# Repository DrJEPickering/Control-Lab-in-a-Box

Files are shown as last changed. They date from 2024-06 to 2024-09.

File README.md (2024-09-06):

Open in MATLAB Online (https://matlab.mathworks.com/open/github/v1?repo=DrJEPickering/Control-Lab-in-a-Box)

# Control-Lab-in-a-Box (CLB)
Dr James E. pickering, Aston University, Birmingham, United Kingdom
<br />E-mail: j.pickering1@aston.ac.uk

# Contents
<br />1.0 Aim of CLB
<br />2.0 Setting-Up
<br />3.0 Teaching Curriculum
<br />4.0 CLB Exercises 
<br />5.0 Trial CLB for Educators and Industry
<br />6.0 Publications Leading to the Development of CLB
<br />7.0 Other MATLAB and Simulink Projects of Interest
<br />8.0 Acknowledgements

## 1.0 Aim of CLB
CLB has been designed to: 
* Bridge the gap between control theory and practice
* Ensure that the skills and knowledge acquired from CLB are transferable, such as to a robotic platform
* Facilitate an incremental and practical approach to learning
* Teach students industry relevant processes and softwares 
* Be easily stored in a lab or office and portable enough to fit within a typical bag
* Affordable (approximately £100), thus reducing concerns if parts are broken or lost

  Presentation2 (https://youtu.be/RAiwTbeBUcU)

## 2.0 Setting-Up 
The computer-aided design (CAD) illustration below displays the setup of the Control-Lab-in-a-Box (CLB) with key components labeled. Please note that not all components are detailed in this diagram, e.g., nuts, bolts, and wires.

<br />For the CLB, rapid prototyping methods of 3D printing and laser cutting are employed, with the the 3D printing CAD files available [here](https://github.com/DrJEPickering/Control-Lab-in-a-Box/blob/main/CAD_files_for_3D_printing.zip) and the laser cutting CAD files available [here](https://github.com/DrJEPickering/Control-Lab-in-a-Box/blob/main/CAD_files_to_be_laser_cut.zip). For the CAD files, Solidworks 2023 files are provided, along with the correspondng STL files.

<br />A document detailing the parts/components necessary for the full utilisation of CLB is provided [here](https://github.com/DrJEPickering/Control-Lab-in-a-Box/blob/main/CLB_component_details.pdf). Additionally, a document detailing the assembly instructions and modifications for parts/components is included [here](https://github.com/DrJEPickering/Control-Lab-in-a-Box/blob/main/Assembly_modifications_Instructions.pdf)
 
ECC_2024_CLB_V4

## 3.0 Teaching Curriculum
The table below presents a schedule for integrating the Control-Lab-in-a-Box (CLB) exercises into the teaching of control engineering theory and simulation. Although the notes for theory and simulation are not provided on this page, they are available upon request via email.

Additionally, the MathWorks Onramp self-paced online courses for MATLAB and Simulink, used in the teaching curriculum, can be accessed through the provided [link](https://matlabacademy.mathworks.com/). 
The DC motor virtual lab is also available at the specified [link](https://uk.mathworks.com/matlabcentral/fileexchange/100064-virtual-hardware-and-labs-for-controls).

ECC_2024_CLB_V4

## 4.0 CLB Exercises 
Control-Lab-in-a-Box (CLB) is used for nine exercises (available to download via the links beneaf the illustration below), with these detailed via the illustration below. For the nine CLB exercises, Simulink Arduino Support Package is used, details can be found [here](https://uk.mathworks.com/hardware-support/arduino.html?#simulink). Details on how to install the Add-on (i.e., Simulink Arduino Support Package) can be found within CLB-1 (i.e., Simulink for Code Generation and Deployment: LED Exercise).

ECC_2024_CLB_V4

<br /> The nine CLB exercises can be viewed below:
<br />[CLB-1.1: Simulink for Code Generation and Deployment: LED Exercises](https://github.com/DrJEPickering/Control-Lab-in-a-Box/blob/main/CLB_1.1_Simulink%20for%20Code%20Generation%20and%20Deployment%20LED%20Exercise.pdf)
<br />[CLB-2.1: DC motor on/off, PWM and polarity control](https://github.com/DrJEPickering/Control-Lab-in-a-Box/blob/main/CLB_2.1_Polarity_speed_control_DC_motor.pdf)
<br />[CLB-3.1: Temperature sensor TMP36 and low pass filter](https://github.com/DrJEPickering/Control-Lab-in-a-Box/blob/main/CLB_3.1_Temp_sensor_filtered.pdf)
<br />[CLB-3.2: Ultrasonic sensor](https://github.com/DrJEPickering/Control-Lab-in-a-Box/blob/main/CLB_3.2_Ultrasonic_sensor.pdf)
<br />[CLB-3.3: DC motor with an encoder (Hall Effect Sensor)](https://github.com/DrJEPickering/Control-Lab-in-a-Box/blob/main/CLB_3.3%20dc_motor_encoder.pdf)
<br />CLB-4.1: TO be added SOON - DC motor proportional (P) speed control
<br />[CLB-4.2: Least squares for parameter estimation of a DC motor](https://github.com/DrJEPickering/Control-Lab-in-a-Box/blob/main/CLB_4.2%20system_indentification_for_parameter_estimation_dc_motor.pdf)
<br />[CLB-4.3: DC motor proportional and integral (PI) speed control](https://github.com/DrJEPickering/Control-Lab-in-a-Box/blob/main/CLB_4.3%20PI_control_of_a_DC_motor.pdf)
<br />[CLB-4.4: DC motor PI speed control with on/off safety aspects](https://github.com/DrJEPickering/Control-Lab-in-a-Box/blob/main/CLB_4.4%20Temp_disp_control_of_a_DC_motor.pdf)

For the above exercises, this [document](https://github.com/DrJEPickering/Control-Lab-in-a-Box/blob/main/compartment_part_details.pdf) will help when constructing the CLB rigs and perhaps also the CLB Components Details [document](https://github.com/DrJEPickering/Control-Lab-in-a-Box/blob/main/Assembly_modifications_Instructions.pdf).

## 5.0 Trial CLB for Educators and Industry
If you are interested in trying out CLB, we can post it to you. 
We kindly request that you return the box within a reasonable time period (e.g., 3 months) and provide user feedback. 
Please contact Dr. James E. Pickering via email at j.pickering1@aston.ac.uk.

If you do not have a MATLAB licence, a basic version of MATLAB Online is availble free. This provides 20 hours per month of free use and access to 10 commonly used products, see [link](https://uk.mathworks.com/products/matlab-online/matlab-online-versions.html).

## 6.0 Publications Leading to the Development of CLB
[Pickering, J.E. (2024). Developments in Control Engineering Education: Lab-in-a-Box Project Based Learning. In 2024 UKACC 14th International Conference on Control (CONTROL) (pp. 195-200). IEEE.](https://ieeexplore.ieee.org/document/10531946)

[Pickering, J.E. (2024). Control-Lab-in-a-Box: Bridging the Gap between Control Theory and Engineering Practice. UK and Ireland Engineering Education Research Network Conference Proceedings 2023.](https://journals.warwick.ac.uk/index.php/eern/article/view/1621)

## 7.0 Other MATLAB and Simulink Projects of Interest
[Arduino-based-bi-copter-experiments](https://github.com/eenikov/Arduino-based-bi-copter-experiments/tree/main)\
[Robotics 311: How to Build Robots and Make Them Move](https://github.com/michiganrobotics/rob311)

## Acknowledgments
Dr James E. Pickering wishes to acknowledge the following colleagues at Aston University for their help in developing Control-Lab-in-a-Box (CLB): Prof Keith J. Burnham, Aaisha Yasir (Design Intern), Stuart Hallard (Technician), David Palmer (Technician) and Amarjit Dhugga (Technician).

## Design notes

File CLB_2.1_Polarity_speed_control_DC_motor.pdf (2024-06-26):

# DC Motors On/Off, PWM and

# Contents

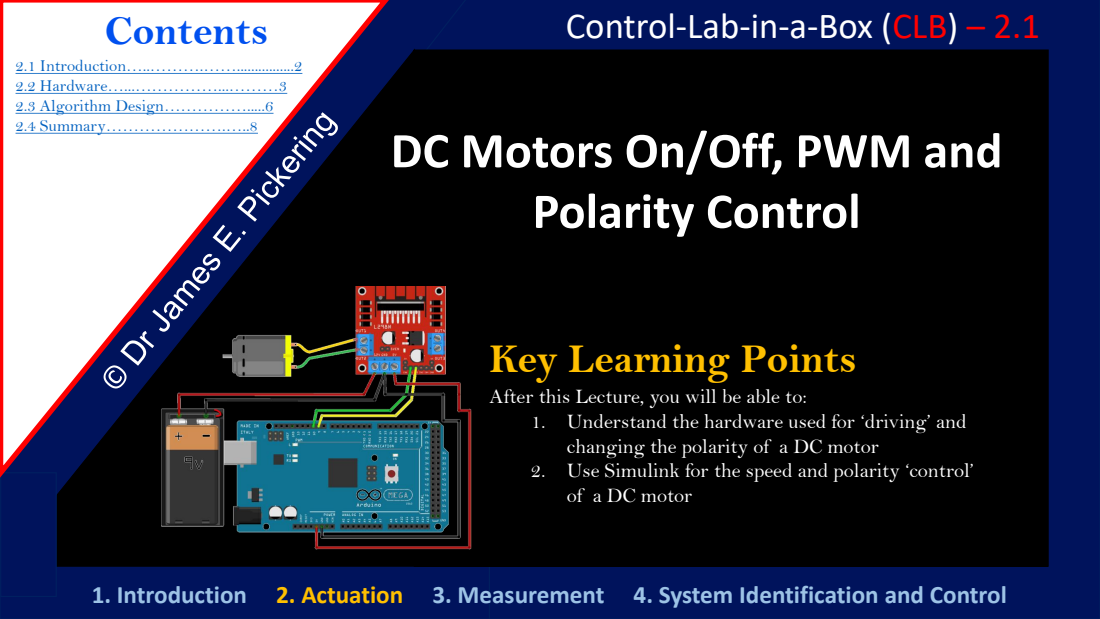
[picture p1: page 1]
Polarity Control; 2.1 Introduction…..……….……................2 2.2 Hardware…...……………...………3 2.3 Algorithm Design…………….....6 2.4 Summary………………….…..8; 1. Introduction 2. Actuation; 3. Measurement 4. System Identification and Control

Control-Lab-in-a-Box (CLB) – 2.1

Key Learning Points

After this Lecture, you will be able to:
1. Understand the hardware used for ‘driving’ and
changing the polarity of a DC motor
2. Use Simulink for the speed and polarity ‘control’
of a DC motor

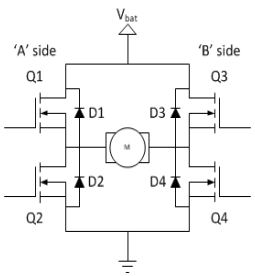
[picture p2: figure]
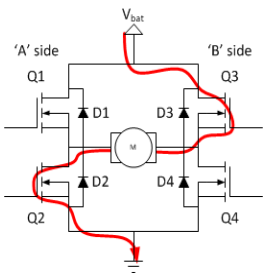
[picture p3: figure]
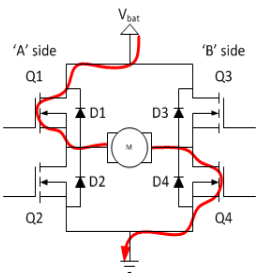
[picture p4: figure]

### 2.1 Introduction ▪ A H-bridge is an electronic

circuit that switches the
polarity of a voltage applied to a load, e.g., a DC motor

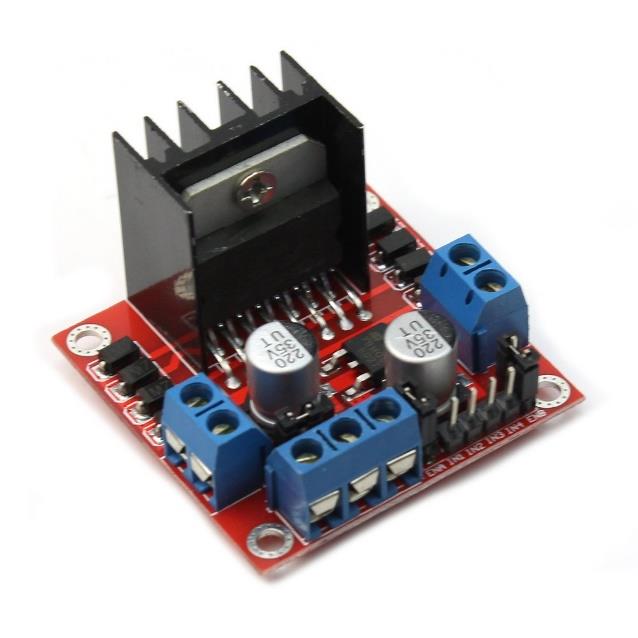
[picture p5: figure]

- The configuration of a H
bridge contains four switches, with the load at the centre, hence the H

-bridge
configuration
- All four switches can be turned on and off independently

© Dr James E. Pickering

DC Motor: PWM
& H

-Bridge

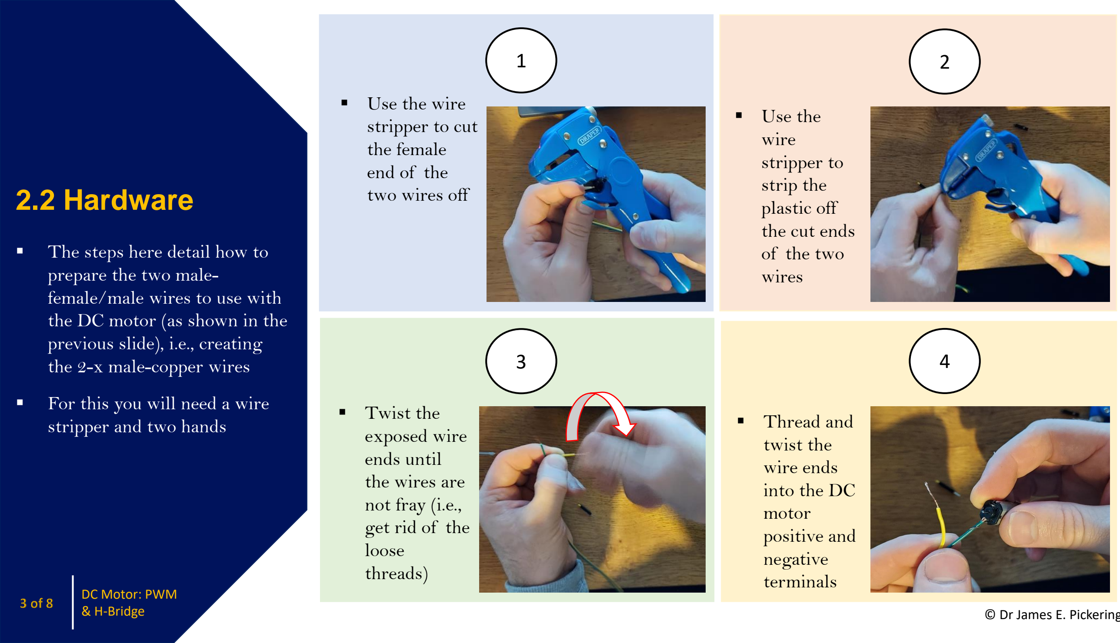
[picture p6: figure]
prepare the two male; - female/male wires to use with the DC motor (as shown in the previous slide), i.e., creating the 2; -x male; -copper wires; ▪ For this you will need a wire stripper and two hands; ▪ Use the wire stripper to strip the plastic off the cut ends of the two wires; ▪ Use the wire stripper to cut the female end of the two wires off; ▪ Twist the exposed wire ends until the wires are not fray (i.e., get rid of the loose threads); ▪ Thread and twist the wire ends into the DC motor positive and negative terminals; -Bridge

### 2.2 Hardware ▪ The steps here detail how to

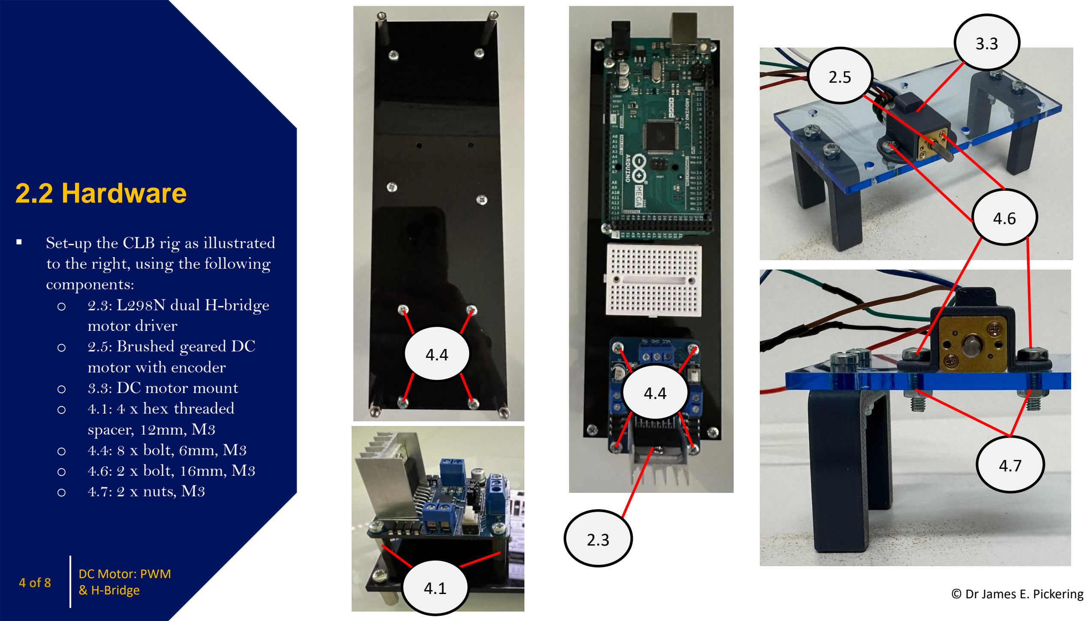
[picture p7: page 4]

### 2.2 Hardware ▪ Set-up the CLB rig as illustrated

to the right, using the following
components: o | | | 2.3: L298N dual H
-bridge
| | | motor driver
- 2.5: Brushed geared DC
| | | motor with encoder
- | 3.3: DC motor mount o | 4.1: 4 x hex threaded
| | | spacer, 12mm, M3
- | 4.4: 8 x bolt, 6mm, M3 o | 4.6: 2 x bolt, 16mm, M3 o | 4.7: 2 x nuts, M3
-Bridge | © Dr James E. Pickering

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
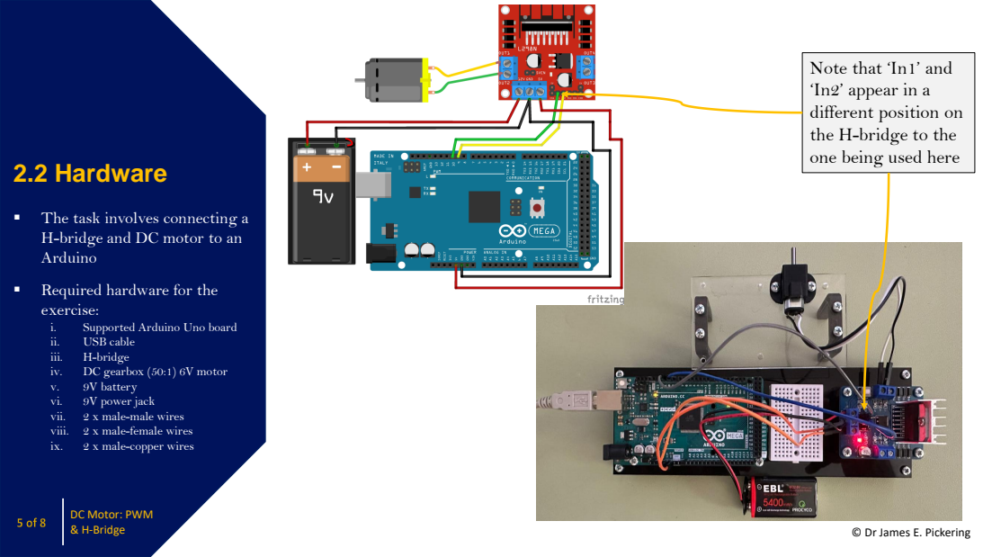
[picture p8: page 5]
2.2 Hardware ▪; The task involves connecting a H-bridge and DC motor to an; Arduino; USB cable; -bridge; DC gearbox; V motor; V battery; V power jack; x male; -male wires; -female wires; -copper wires; -Bridge

Note that ‘In1’ and
‘In2’ appear in a
different position on
the H
one being used here

-bridge to the

▪ Required hardware for the
exercise:
i. Supported Arduino Uno board
iii.
vii.
viii.

## 2.3 Algorithm Design

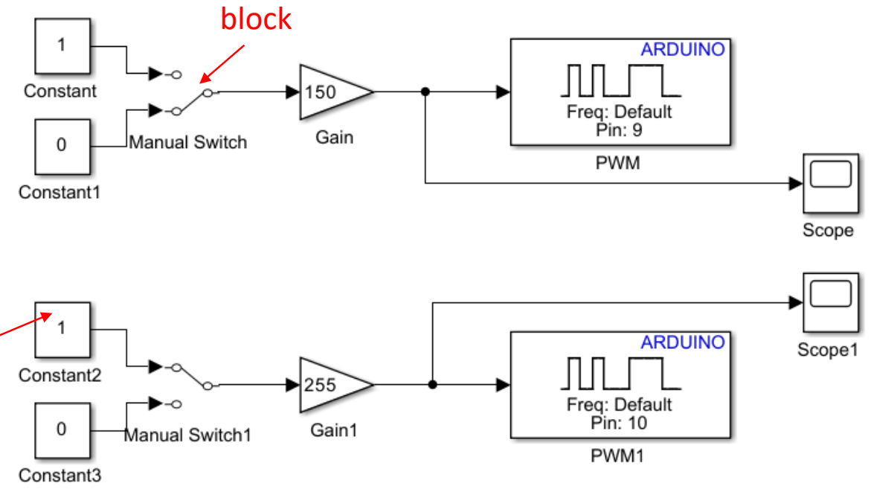
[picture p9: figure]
block

- The Simulink block diagram for the H-bridge algorithm design is given
- The logic for operating the ‘forward’ and ‘reverse’ motion of the DC motor is given
- Note that to realise this in real-time on a system, the switches would need to be external
- Logic of the H-bridge working: Forward
IN1 -> High
IN2 -> Low
Reverse
IN1 -> Low
IN2 -> High
Stop
Both are Low or High

& H-Bridge

### ‘Constant’ block

### ‘Manual Switch’

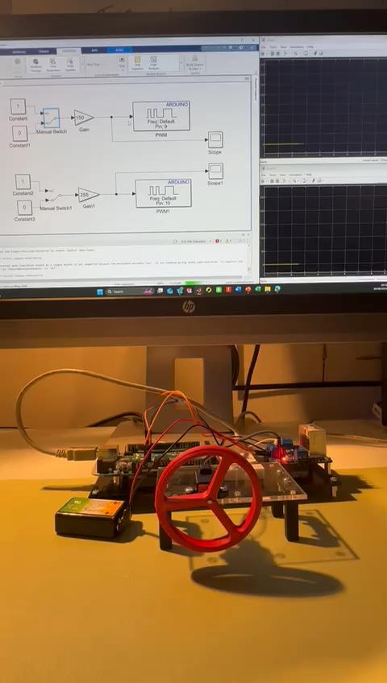
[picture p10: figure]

## 2.3 Algorithm Design

- Combines the pulse width modulation (PWM) and H-bridge

& H-Bridge

Control-Lab-in-a-Box (CLB): DC Motors On/Off, PWM
and Polarity Control

# Contents

# DC Motors On/Off, PWM and

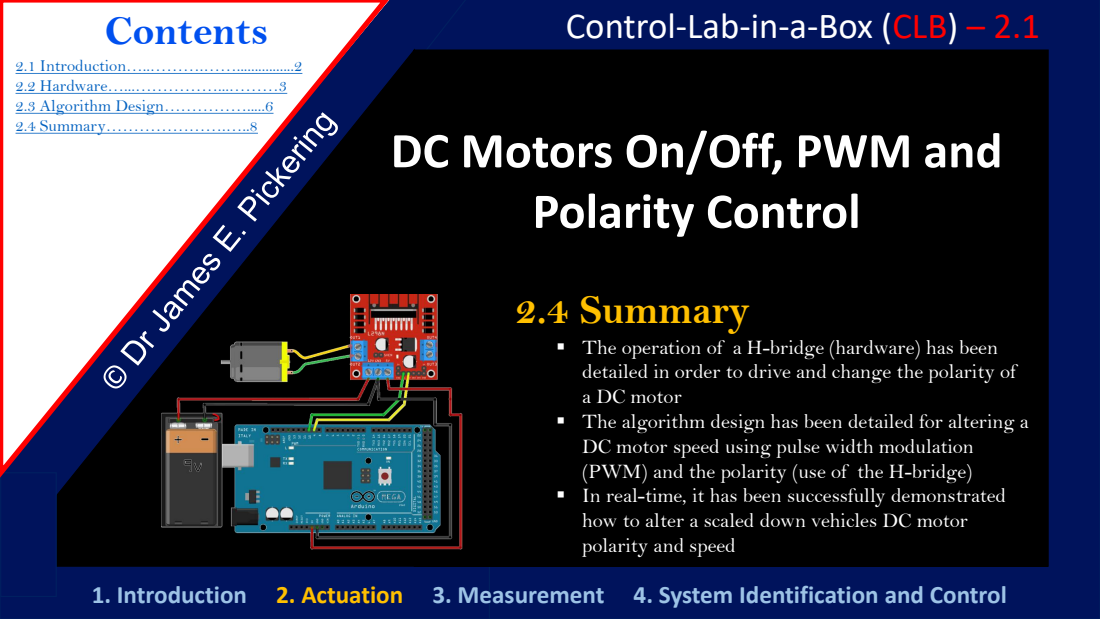
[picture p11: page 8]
2.4 Summary; 2.1 Introduction…..……….……................2 2.2 Hardware…...……………...………3 2.3 Algorithm Design…………….....6 2.4 Summary………………….…..8; 1. Introduction 2. Actuation; 3. Measurement 4. System Identification and Control; Polarity Control

Control-Lab-in-a-Box (CLB) – 2.1

▪ The operation of a H-bridge (hardware) has been
detailed in order to drive and change the polarity of
a DC motor
▪ The algorithm design has been detailed for altering a
DC motor speed using pulse width modulation
(PWM) and the polarity (use of the H-bridge)
▪ In real-time, it has been successfully demonstrated
how to alter a scaled down vehicles DC motor
polarity and speed

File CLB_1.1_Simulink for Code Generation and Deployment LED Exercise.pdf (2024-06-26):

# Simulink for Code Generation and

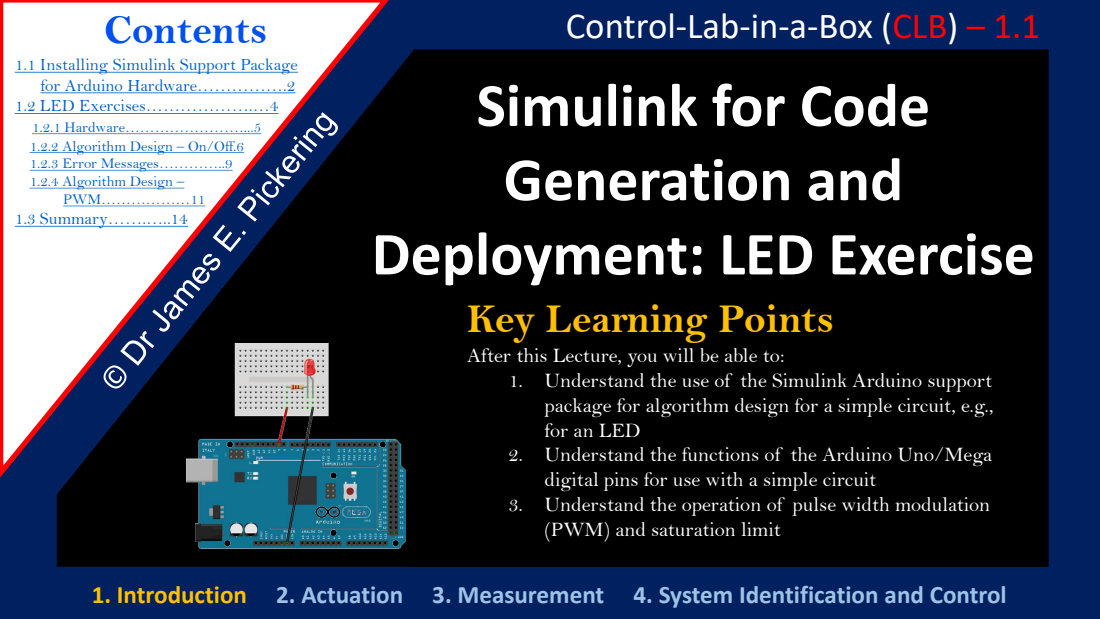
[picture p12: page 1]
1. Introduction 2. Actuation; 3. Measurement 4. System Identification and Control; Contents; 1.2.4 Algorithm Design –

Control-Lab-in-a-Box (CLB) – 1.1

1.1 Installing Simulink Support Package

1.2.2 Algorithm Design – On/Off.6

Deployment: LED Exercise

Key Learning Points

After this Lecture, you will be able to:
1. Understand the use of the Simulink Arduino support
package for algorithm design for a simple circuit, e.g.,
for an LED
2. Understand the functions of the Arduino Uno/Mega
digital pins for use with a simple circuit
3. Understand the operation of pulse width modulation
(PWM) and saturation limit

# 1.1 Installing Simulink Support Package for Arduino Hardware

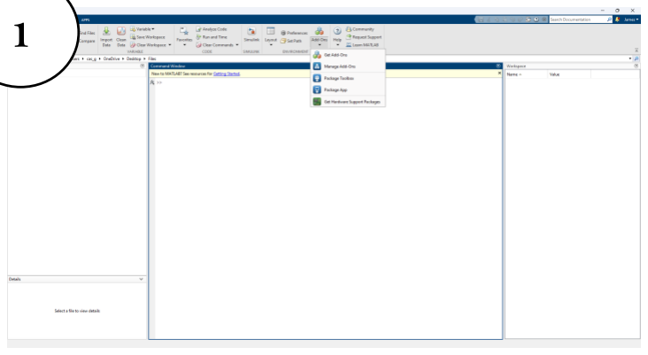
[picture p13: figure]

## - Undertake the following steps:

## 1) Click on ‘Add-Ons’ on the Toolbar and then ‘Get Hardware Support Package’

## 2) Search for the ‘Simulink Support Package for Arduino Hardware’ and click on it

## 3) Then click on ‘Install’ and then follow

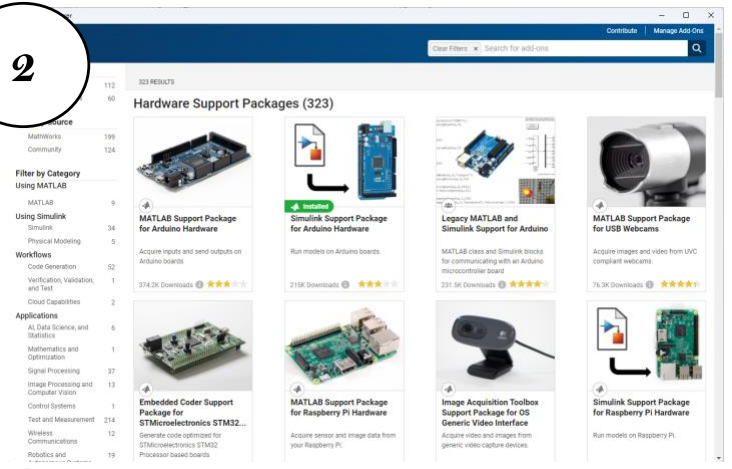
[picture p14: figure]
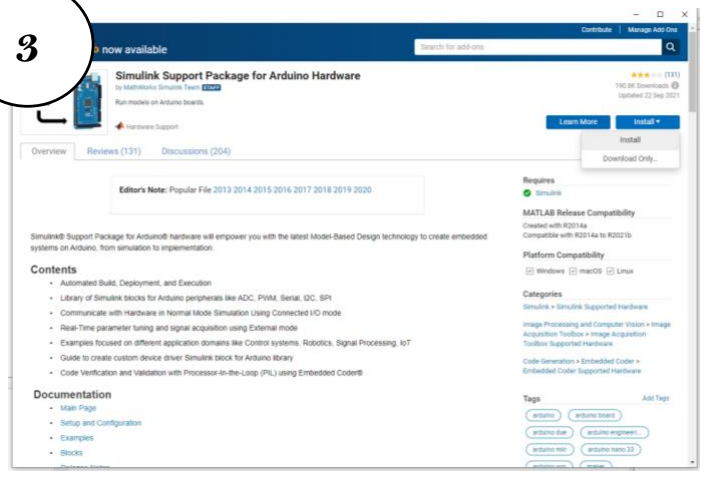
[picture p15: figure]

the steps-through | 3

© Dr James E. Pickering

Simulink for Autocode
Generation: LED
Exercise

## - Undertake the following steps: 4) After opening a ‘Blank Model’ within Simulink, open the ‘Library Browser’ – the

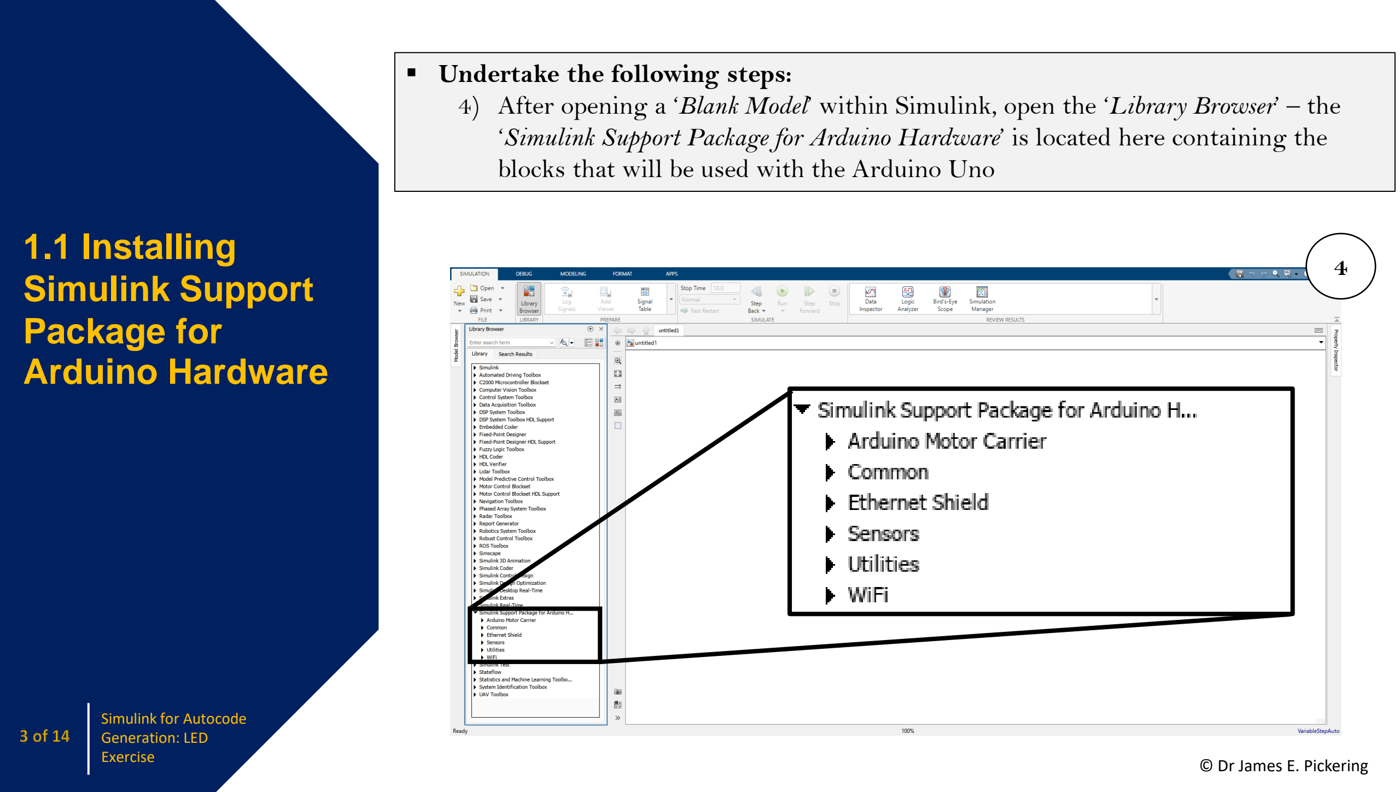
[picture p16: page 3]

## ‘Simulink Support Package for Arduino Hardware’ is located here containing the blocks that will be used with the Arduino Uno

# 1.1 Installing Simulink Support Package for Arduino Hardware

4

Simulink for Autocode

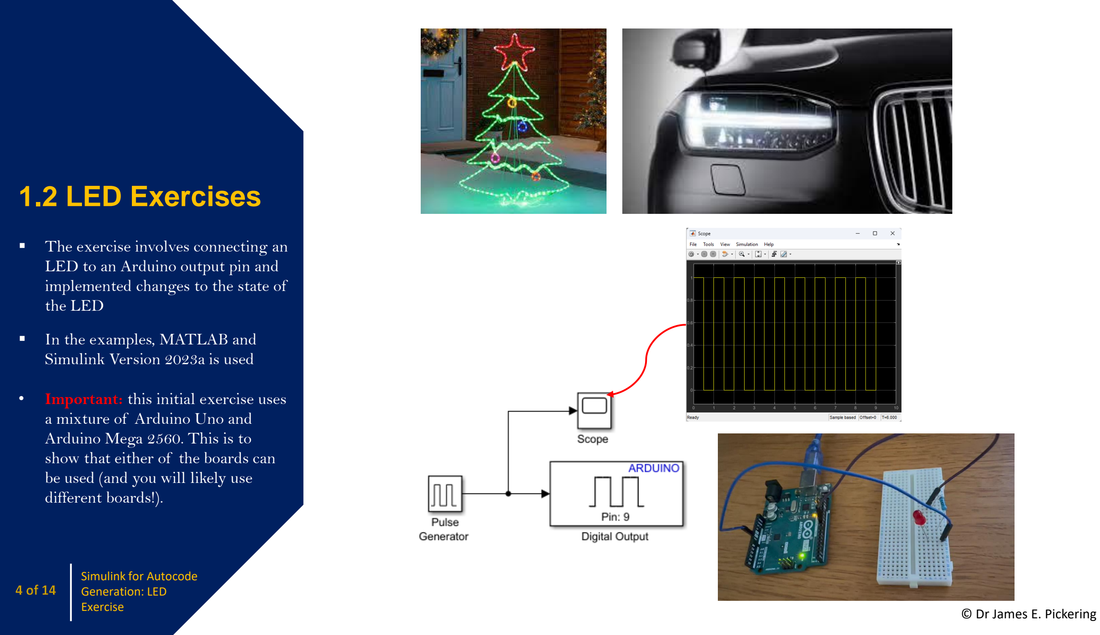
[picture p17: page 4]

### 1.2 LED Exercises ▪ The exercise involves connecting an

LED to an Arduino output pin and implemented changes to the state of the LED

- In the examples, MATLAB and Simulink Version 2023a is used
- Important: this initial exercise uses a mixture of Arduino Uno and Arduino Mega 2560. This is to show that either of the boards can be used (and you will likely use different boards!).

Simulink for Autocode

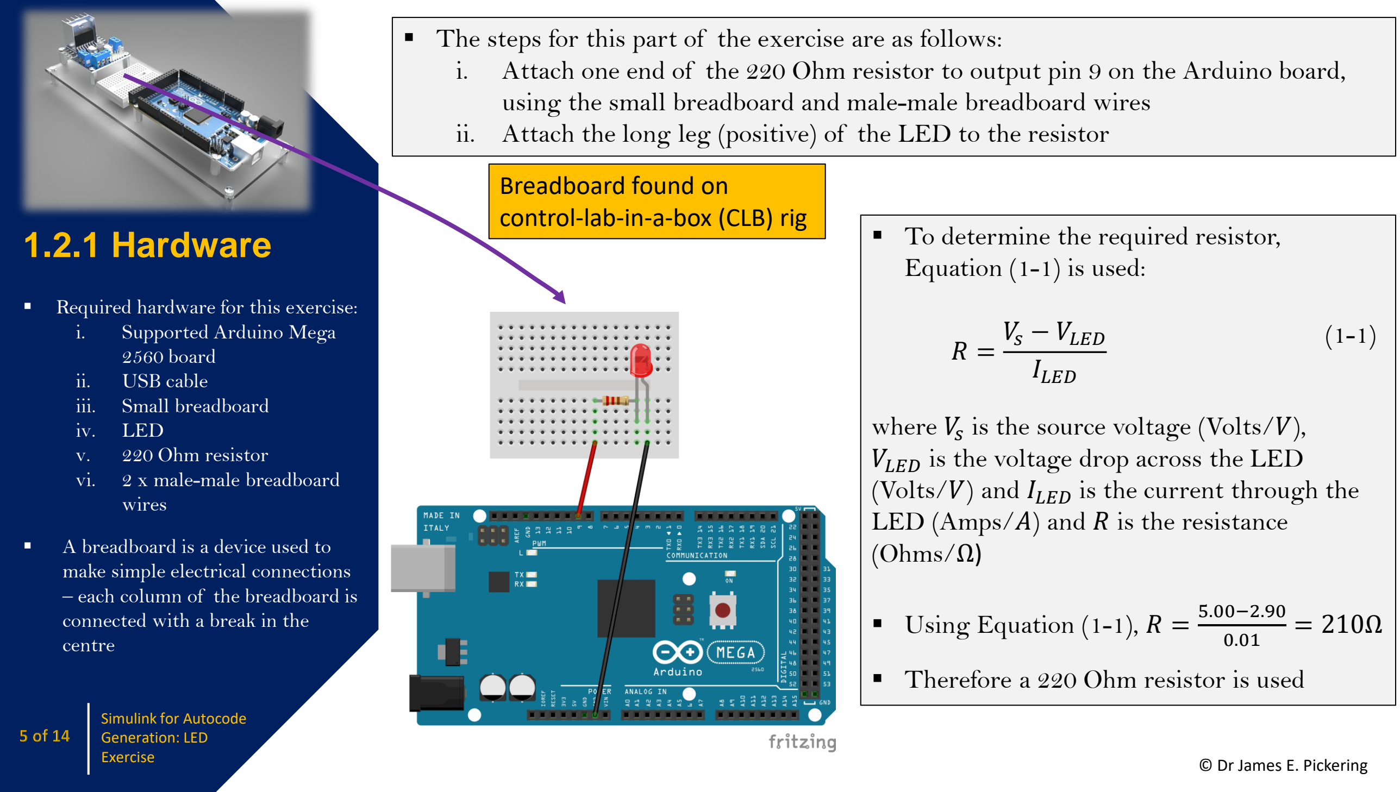
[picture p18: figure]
1.2.1 Hardware; ▪ Required hardware for this exercise: i. Supported Arduino Mega 2560 board; USB cable; iii.; Small breadboard; LED; v. 220 Ohm resistor; 2 x male-male breadboard; wires; ▪ A breadboard is a device used to make simple electrical connections – each column of the breadboard is connected with a break in the centre; ▪ To determine the required resistor, Equation (1-1) is used:; where Vs; is the source voltage (Volts/V), VLED is the voltage drop across the LED; LED (Amps/A) and R is the resistance (Ohms/Ω); ▪ Using Equation (1-1), R =; ▪ Therefore a 220 Ohm resistor is used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

## - The steps for this part of the exercise are as follows:

i. Attach one end of the 220 Ohm resistor to output pin 9 on the Arduino board,

## using the small breadboard and male-male breadboard wires ii. Attach the long leg (positive) of the LED to the resistor

## (Volts/V) and ILED is the current through the

# 1.2.2 Algorithm

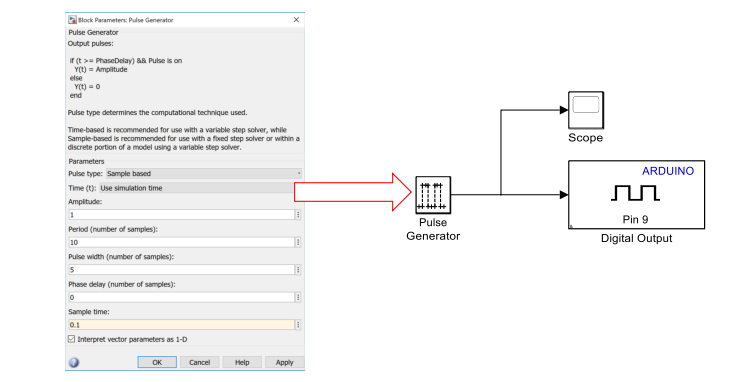
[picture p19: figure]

# Design – On/Off

- In this part of the exercise a Simulink model will be
developed to change the state of the Arduino digital output to being either on or off

- The steps for this part of the exercise are as follows: i. Set-up the pulse generator as shown below (found in ‘Sources’) and connect this to a digital output block (found under ‘Common’ in the ‘Simulink Support Package for Arduino Hardware’), with a scope connected (found in ‘Sinks’) ii. Amplitude of 1 implied a value of 5V will be supplied to Pin 9 (by default the ‘Digital Output’ block will be Pin 9)

Simulink for Autocode

# 1.2.2 Algorithm Design – On/Off

- In this part of the exercise, the Simulink model will be
configured and run on the
supported Arduino Uno/Mega board
- Important: make sure
MATLAB is operating/saving in a suitable working directory before clicking ‘Run’
1. Connect the Arduino board to your computer with a USB cable
2. When on your Simulink Window, click on ‘Modelling ‘ and then ‘Model Settings’ to open ‘Configuration Parameters’
3. Select the ‘Hardware Implementation’ panel and within the ‘Hardware Board’ tab, select the ‘Arduino Uno’ (or Arduino Mega 2560 – depending on the board being used) hardware from the ‘Hardware Board’ list, then click ‘Apply’ and then ‘OK’
4. Now in your Simulink model, the ‘Hardware’ tab will appear (Note: your Simulink model should be developed before undertaking this step). You should see the ‘Arduino Board’. Now change the simulation stop time to ‘inf ’ (infinity) and then click ‘Monitor & Tune’. The Simulink model (algorithm design) will now be deployed (converted to C code) to the connected Arduino hardware.
5. Look at the LED attached to pin 9. The LED should blink once time every second.
6. See the next slide if you’re experiencing errors

2 & 3

Linked board | Simulation stop time (i.e., infinity’)

4

## Embed code

Simulink for Autocode

## Arduino Mega 2560 can also be selected here

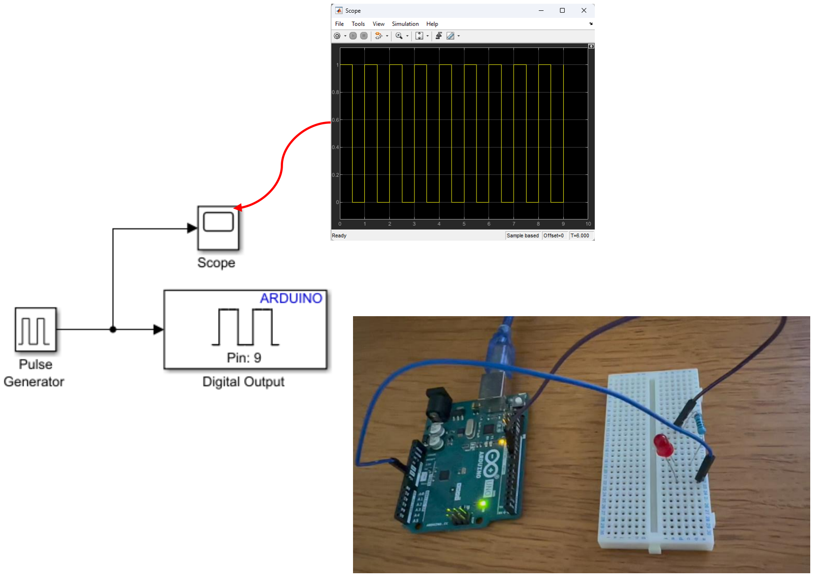
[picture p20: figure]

# 1.2.2 Algorithm Design – On/Off

Simulink for Autocode

1

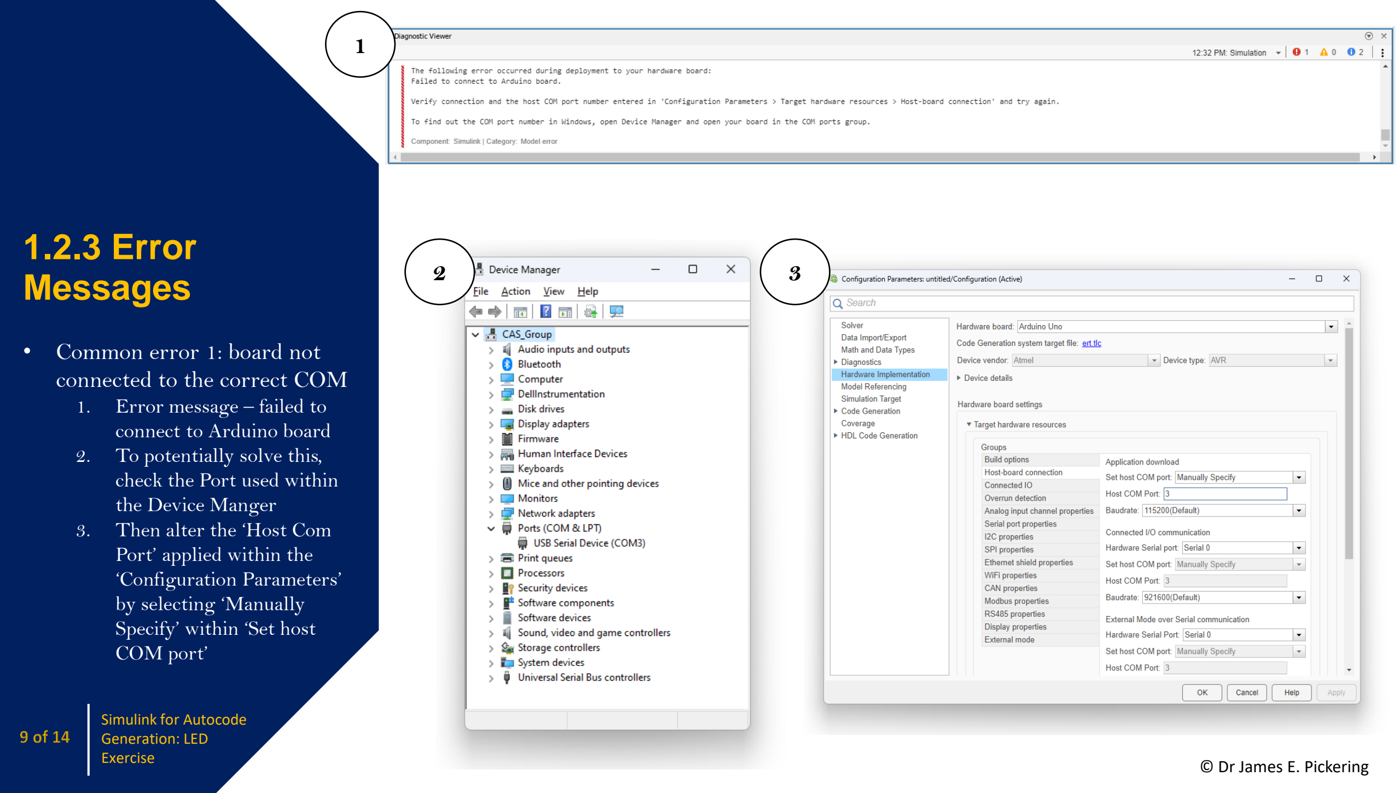
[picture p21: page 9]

# 1.2.3 Error

Messages • Common error 1: board not

connected to the correct COM
1. Error message

– failed to
connect to Arduino board
2. To potentially solve this, check the Port used within the Device Manger
3. Then alter the ‘Host Com Port’ applied within the
‘Configuration Parameters’ by selecting ‘Manually
Specify’ within ‘Set host
COM port’

2

3

Simulink for Autocode

1

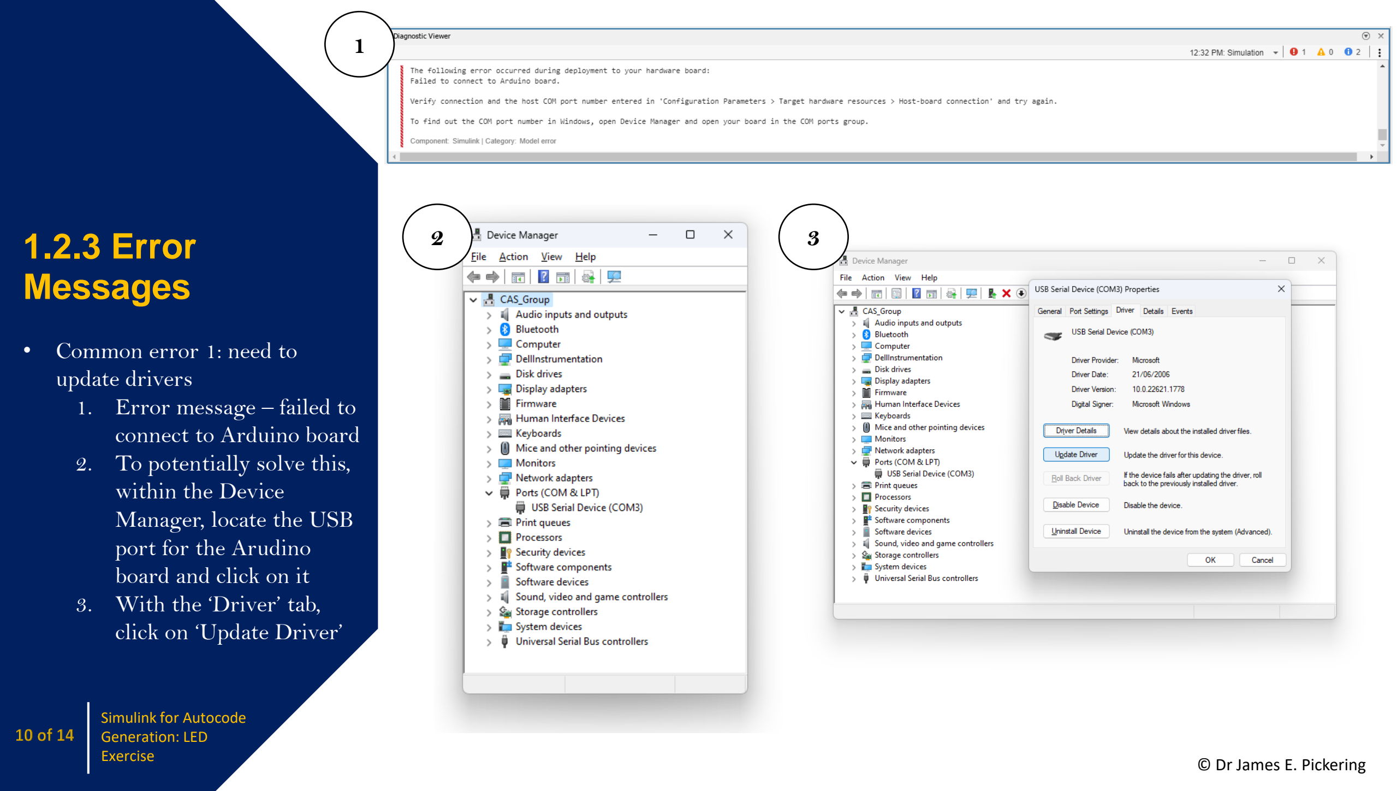
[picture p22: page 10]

# 1.2.3 Error

Messages • Common error 1: need to

update drivers
1. Error message

– failed to
connect to Arduino board
2. To potentially solve this, within the Device
Manager, locate the USB
port for the Arudino
board and click on it
3. With the ‘Driver’ tab,
click on ‘Update Driver’

2

3

Simulink for Autocode

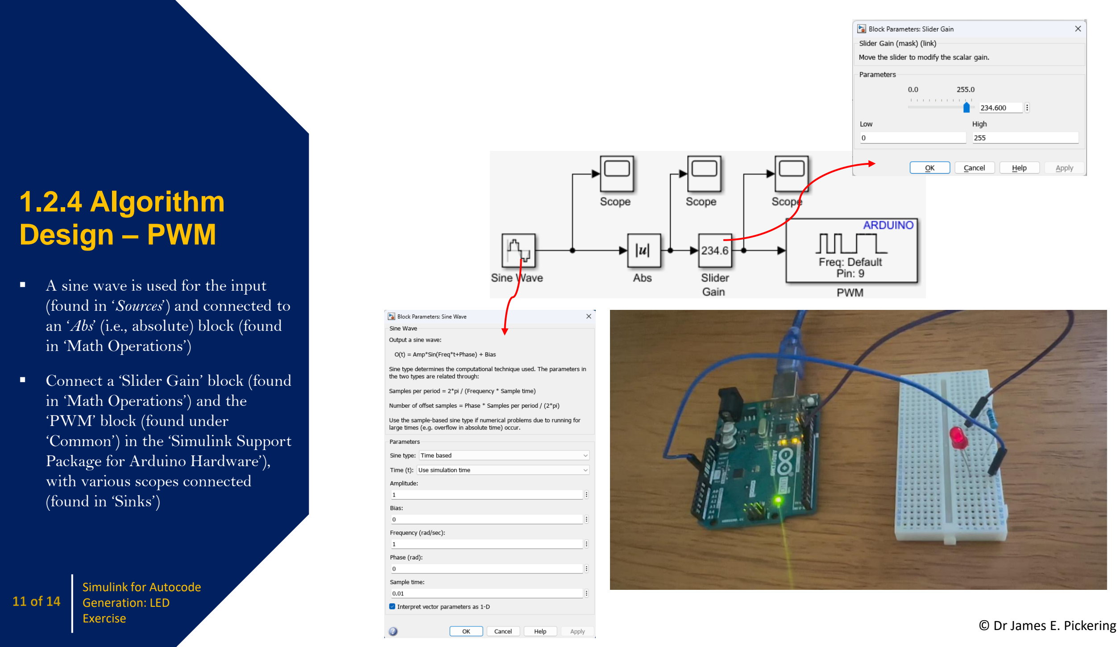
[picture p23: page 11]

# 1.2.4 Algorithm Design

# – PWM

- A sine wave is used for the input (found in ‘Sources’) and connected to an ‘Abs’ (i.e., absolute) block (found in ‘Math Operations’)
- Connect a ‘Slider Gain’ block (found in ‘Math Operations’) and the ‘PWM’ block (found under
‘Common’) in the ‘Simulink Support Package for Arduino Hardware’), with various scopes connected (found in ‘Sinks’)

Simulink for Autocode

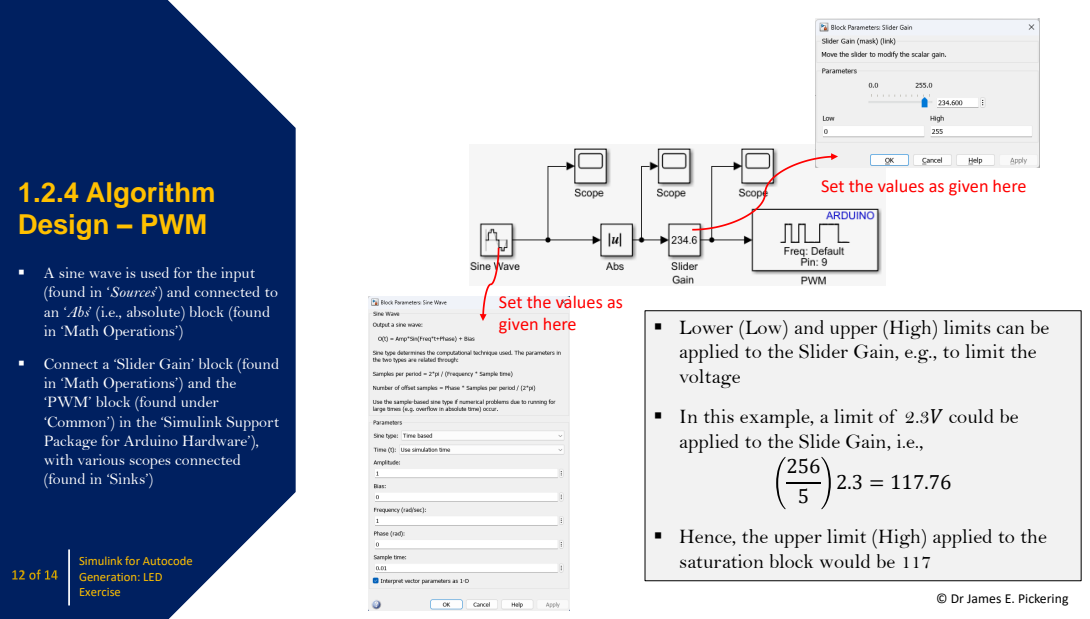
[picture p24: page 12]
1.2.4 Algorithm Design; – PWM; V could be; Simulink for Autocode; saturation block would be 117

Set the values as given here

▪ A sine wave is used for the input
(found in ‘Sources’) and connected to
an ‘Abs’ (i.e., absolute) block (found
in ‘Math Operations’)

Set the values as
given here

▪ Lower (Low) and upper (High) limits can be
applied to the Slider Gain, e.g., to limit the
voltage

▪ Connect a ‘Slider Gain’ block (found
in ‘Math Operations’) and the
‘PWM’ block (found under
‘Common’) in the ‘Simulink Support
Package for Arduino Hardware’),
with various scopes connected
(found in ‘Sinks’)

▪ In this example, a limit of 2.3
applied to the Slide Gain, i.e.,

▪ Hence, the upper limit (High) applied to the

1.2.4 Algorithm Design; – PWM; Useful setting 1; Useful setting 2

▪ A sine wave is used for the input
(found in ‘Sources’) and connected to
an ‘Abs’ (i.e., absolute) block (found
in ‘Math Operations’)

▪ Connect a ‘Slider Gain’ block (found
in ‘Math Operations’) and the
‘PWM’ block (found under
‘Common’) in the ‘Simulink Support
Package for Arduino Hardware’),
with various scopes connected
(found in ‘Sinks’)

Simulink for Autocode

# Simulink for Autocode

# Contents

1.3 Summary; 1.3 Summary…….…..14; 1. Introduction 2. Actuation; 3. Measurement 4. System Identification and Control

Control-Lab-in-a-Box (CLB) – 1.1

1.1 Installing Simulink Support Package
for Arduino Hardware…………….2
1.2 LED Exercises……………….…4
1.2.1 Hardware……………………...5
1.2.2 Algorithm Design – On/Off.6
1.2.3 Error Messages…………..9
1.2.4 Algorithm Design –
PWM………………11

Generation: LED Exercise

▪ Simulink has been used along with an Arduino Uno/Mega to
develop the algorithm design for a simple circuit (resistor and
LED) hardware set-up
▪ Initial example detailed the on/off operation of the LED
▪ The use of pulse width modulation (PWM) has then been
applied for varying brightness of the LED
▪ A saturation limit has been applied within the algorithm
design to limit the voltage

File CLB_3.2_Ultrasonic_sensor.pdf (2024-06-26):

# Contents

# Control-Lab-in-a-Box (CLB) – 3.2

Ultrasonic Sensor; 1. Introduction 2. Actuation; 3. Measurement 4. System Identification and Control

3.4 Algorithm Design – Data

Key Learning Points

After this Lecture, you will be able to:
▪ Obtain measured distance values from the
ultrasonic sensor, and undertake the process of data
rejection for ‘unwanted’ data points


## 3.1 Introduction

- Required hardware for the exercise:
✓ | Supported | Arduino
Uno board
✓ | USB cable
✓ | Breadboard
✓ | Ultrasonic HC-SR04
sensor
✓ | 4 | x | male-to-male
wires

© Dr James E. Pickering

Ultrasonic Sensor

d =

Calculation for distance measurement: | 1 tc 2

Speed of sound (approximately 343m/s)

(halved as t is time
of Trig and Echo)

Time
(between Trig and Echo)

Distance

HC-SR04 ultrasonic sensor details:
- Distance measurement of 0.02 to 4.00m
- Accuracy of ±0.003m

Transmitter

Receiver

Object

Original wave (Trig)

Reflected wave (Echo)


3.2 Hardware ▪ | Required hardware for the exercise: ✓ | Supported | Arduino | Mega

2560 board
✓ | USB cable ✓ | Breadboard ✓ | Ultrasonic HC

-SR04 sensor
✓
4

x male

-to

-female wires

- Set
-up the CLB rig as illustrated to the right, using the following
components of importance: o | | | 2.8: HC-SR04 ultrasonic
| | | sensor
- 3.5: Ultrasonic sensor and
| | | LEDs mount
- | 4.6: 2 x bolt, 16mm, M3 o | 4.7: 2 x nuts, M3

4.6
4.7

3.5

2.8


## 3.3 Algorithm Design

- ‘Ultrasonic Sensor’ block is found under the ‘Sensors’ tab in ‘Simulink Support Package for Arduino Hardware’
- ‘Display’ and ‘Scope’ are both found under the ‘Sinks’ tab in ‘Simulink’
- Undertake the following three steps:
i. Double click on ‘Ultrasonic Sensor’ then set the number of signal pins to ‘2’ ii. The trigger pin should be defined as ‘4’ and the echo pin as ‘5’
iii. Select a sampling time/interval, Ts
(e.g., 0.01 seconds – you should investigate different values)


Move an object Infront
of the ultrasonic
sensor to measure the
distance.


## 3.4 Algorithm Design – Data Rejection

- This could be set-up for use within the operational
requirenents of the sensor, i.e., 0.02 to 4.00m


- ‘Switch’ block is found in ‘Signal Routing’ of ‘Switch’
- ‘Memory’ block is found in ‘Discrete’ of ‘Simulink’
- Undertake the following step:
i. Double click on the ‘Switch’ and change the ‘Threshold’ to 0.1 (how this set-up works: if the ultrasonic sensor output value is above 0.1 meters, then the last known stored value in the memory below 0.1 meters will be the output)

# Ultrasonic Sensor

# Contents

3.5 Summary; 1. Introduction 2. Actuation; 3. Measurement 4. System Identification and Control

Control-Lab-in-a-Box (CLB) – 3.2

3.1 Introduction………………...…….2
3.2 Hardware………………….……3
3.3 Algorithm Design……..…….4
3.4 Algorithm Design – Data
Rejection……………..…5
3.5 Summary……………..6

▪ An ultrasonic distance measuring sensor has been
used with an Arduino Uno
▪ Simulink has then been used to develop a data
rejection algorithm to reject ‘unwanted’ data
points

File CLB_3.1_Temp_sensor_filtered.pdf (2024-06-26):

# Temperature Sensor TMP36

# Contents

1. Introduction 2. Actuation; 3. Measurement 4. System Identification and Control

Control-Lab-in-a-Box (CLB) – 3.3

and Low Pass Filter

Key Learning Points

After this Lecture, you will be able to:
▪ Obtain measured temperature data from
the TMP36 sensor, and undertake the
process of filtering noisy measured data
using a low pass filter


## 3.1 Hardware

- Required hardware for the exercise:
i. | Supported | Arduino | Uno
| board
ii. | USB cable
iii. | Low voltage temperature
sensor (TMP36)
iv. 3 x male-male wires
- Voltage input: 2.7V to 5V
- Operating temperature:
-40°C to +125℃

Temperature Sensor
TMP36 and Low Pass
Filter | © Dr James E. Pickering

Vin

Analogue Vout | GND

Low voltage temperature
sensor (TMP36)

### Use the breadboard on the Control-Lab-in-a-Box (CLB) rig


## 3.2 Algorithm

Design ▪ Output from Pin 4 is a 10

-bit
| analogue value ranging from 0 to
| 1023
- E.g., 150 output from Pin 4, i.e.
| 150
| 102
| 3 =
| 0.146
| 6
| which is basically a ratio between 0 and 1
- Multiplied by 5V (Arduino
| supply) gives: 0.1466 x
| 5 = 0.7330V

Select sampling interval Ts of 0.01 seconds

© Dr James E. Pickering

Temperature Sensor

Filter

150

0.7330V


Sensor | Offset Voltage (V) | Output Voltage mV Scaling ( ) °C | Output Voltage @25°C(mV)
TMP35 | 0 | 10 | 250
TMP36 | 0.5 | 10 | 750
TMP37 | 0 | 20 | 500

## 3.2 Algorithm Design

- TMP36 has a voltage offset of 0.5V (so that negative values can be accounted for), e.g.,

0.7330 − 0.5 = 0.2330V

- The above value is then
multiplied by 100, as the
TMP36 sensor has an output scale factor of 10mV/ °C, e.g., 0.2330 1°C
0..01V

= 23.3°C

© Dr James E. Pickering

Temperature Sensor

150 | 0.7330V 0.2330V | 23.3℃


## 3.2.1 Low Pass Filter (Digital)

- Low pass filter applied (stops high frequencies passing
through)
- A continuous-time transfer function of an RC (time
constant τ) circuit has been discretised using MATLAB
- Ensure the sampling interval Ts used throughout is
consistent

clear; clc; close all;

%% Continuous and Discrete Transfer Function R=1000; % resistor [Ohms]
C=1000*10^(-6); % capacitor [F]
Tau= R*C; % time constant
G = tf([1],[Tau 1]);

T_s = 0.01; % sample interval
Gd = c2d(G,T_s) %ZOH method by default
- The discrete-time transfer function will appear in the command window (insert the values into the ‘Discrete Filter’
- Recall: G s =

1
RCs+1

=

1
τs+1

Temperature Sensor


## 3.2.1 Low Pass Filter (Digital)

- Unfiltered signal is blue, and the filtered signal is white
- By adding the filter, the temperature estimate is much less noisy
- A drawback of the filtering is that it adds a delay/lag (this is visible when inspecting the unfiltered and filtered signal), hence no information is
provided

Temperature Sensor

- Recall:
- Reducing the time constant τ (i.e., RC) will reduce the lag, however the trade-off is that the noise won’t be filtered as well

G s =

1

### RCs + 1

=

1
τs + 1

## 3.2.2 Exercise

- Further task: investigate different sampling intervals Ts and time constants τ
- Fill in the table

Temperature Sensor

### Sample interval, Ts [seconds]

Time constant,

### τ (i.e., RC value)

### Filter lag [seconds]

### Filtering performance [worse/better]

0.01 | 1 | 5 | N/A as baseline

# Temperature Sensor TMP36

# Contents

3.3 Summary; 1. Introduction 2. Actuation; 3. Measurement 4. System Identification and Control

Control-Lab-in-a-Box (CLB) – 3.3

and Low Pass Filter

▪ The low voltage TMP36 temperature sensor has
been used with an Arduino Uno to capture data
(hardware)

▪ Simulink has then been used to develop a signal
processing algorithm to convert the data
outputted from the temperature sensor into a
physical value (i.e., degree Celsius)

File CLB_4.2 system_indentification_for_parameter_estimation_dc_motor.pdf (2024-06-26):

# Least Squares for Parameter

Contents | Control-Lab-in-a-Box (CLB) – 4.2

1. Introduction 2. Actuation; 3. Measurement 4. System Identification and Control

Estimation of a DC Motor

Key Learning Points

After this Lecture, you will be able to understand the following:
1. How to capture input and output data from an DC
motor with an encoder using an Arduino Uno
2. How to use least squares to develop a mathematical
model based on known and measured input and output
data


### 4.1 Introduction ▪ The DC motor will be subject

to a voltage step input, with the revolutions per minute (RPM) output measured using a hall effect sensor

- Based on the known/measured input

-output data, a black

-box
model is to be developed (i.e., not considering the underlying physics of the motor)

– with
the model then used to develop the controller

Least Squares for
Parameter Estimation
of a DC Motor | © Dr James E. Pickering

Encoder A phase
Encoder B phase
Encoder ground
Encoder power
Motor power
Motor ground

K
Ls

+

### R Js

+

b

+

K

2

input

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
# output ω(s)

113.7
s

+

3.398

### input Vin(s)

output

G
a

(

s

)

## 4.1 Introduction

- A Hall effect sensor detects a magnetic field


- The output voltage of a Hall sensor is directly proportional to the strength of the field. It is named for the American
physicist Edwin Hall.
- By detecting the passing of a magnet, the Hall effect sensor generates a pulse-train output

© Dr James E. Pickering

- Hall effects sensors are commonly used to time the speed of wheels and shafts, such as for internal combustion engine ignition timing, tachometers and anti-lock braking systems
- Hall effect sensors are used in brushless DC electric motors to detect the position
- Employing an offset Hall effect sensor can generate a quadrature output for determining the direction of the motion


### Clockwise


### Anti-clockwise

Least Squares for

of a DC Motor


Resolution of 12 impulses per revolution


### 4.1 Introduction ▪ Set-up the CLB rig as illustrated

to the right (the same set

-up as
used in CLB

-3.3), using the
following components: o | | | 2.3: L298N dual H
-bridge
| | | motor driver
- 2.5: Brushed geared DC
| | | motor with encoder
- | 3.3: DC motor mount o | 4.1: 4 x hex threaded spacer,
| | | 12mm, M3
- | 4.4: 8 x bolt, 6mm, M3 o | 4.6: 2 x bolt, 16mm, M3 o | 4.7: 2 x nuts, M3

Least Squares for

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
Circuit diagram given here varies ever so slightly to the motor we are using; 4.2 Hardware; ▪ The task involves connecting a H-bridge and DC motor with an encoder to an Arduino ▪ Required hardware for the exercise:; i. Supported Arduino Mega 2560 board; USB cable; iii.; H-bridge; 6V DC motor with encoder; v. 9V battery; 9V power jack; vii.; Various wires; as DC motor with an encoder (i.e., CLB-3.3); Encoder A phase Encoder B phase Encoder ground Encoder power Motor power Motor ground; Least Squares for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

- Note that this initial part is the same

4.3 Algorithm Design

‘Goto’ blocks are used to capture
the input voltage step data (and on
the next Slide to capture the speed
output data)

▪ A 5 Volt step input is applied
to the DC motor

Within the ‘Scope’ block
‘Configuration Properties’, click
on ‘Logging’ and select ‘Log data
to workspace’ and ‘Save format’ to
‘Structure with time’

Least Squares for

4.3 Algorithm Design; ▪ The encoder on the DC motor is now used to estimate the motor speed based on the encoder counts; ▪ The encoder counts indicate the motors position, hence the motors speed (rate of change of the position) over a specified sample interval can be determined; motor is determined using yk−yk−1; - the; Backward Euler approximation (this converts the signal from counts/second to; position measurement and Ts; is the sample; interval; Least Squares for; exist, it is normal to use z; , where; z the following: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

The change in position (speed) of the DC

revolutions/second), where yk is the current position measurement, yk−1 is the previous

Since the past values of a sampled signal

−1 means shift to k– 1, with this given by gear ratio (i.e., 1:298) and the encoders 12

4.3 Algorithm; Design ▪; Before running the algorithm; Sample interval of 0.01; The three gain terms from the previous slide are ‘lumped’ together

The data observed from the
scope illustrates counts/second
from the DC motor encoder,
with this increasing when the
DC motor is rotating in the
clockwise direction

design on the Arduino, ensure
the following are set:
i. Run time of 1 second
second

‘From’ blocks are used
to capture the input
voltage step data and
the speed output data

From observation
of the output
data (revolutions
per minute), the
response takes
the form of a 1st
order transfer
function

Least Squares for

## 4.4 Least Squares

- Using the known/measured input/output data, Least
squares is used to develop a mathematical model based on initial observations, i.e., the response being that of a 1st order transfer function
- The following code will ‘pick up’ the data from the two
scopes and put this into vector form

clc; close all;
%% Load measured input/output data

y = ScopeData.signals.values;
y = reshape(y,length(y),1);
t = ScopeData.time;
u = ScopeData2.signals.values;
u = reshape(u,length(u),1);

%% Linear least squares to estimate discrete-time model parameters Phi=[-y(1:end-1) u(1:end-1)];
Y=y(2:end);
theta=inv(Phi'*Phi)*Phi'*Y

%% Simulate discrete-time difference model N=length(y);
y_sim=zeros(N,1);
for k=2:1:N
y_sim(k)=[-y_sim(k-1) u(k-1)]*theta; end

Least Squares for

## 4.4 Least Squares

- The actual/physical output is plotted against the estimated model output
- The model fit is evaluated, comparing the measured and simulated output data

%% GRAPHICAL OUTPUTS (MEASURED AND ESTIMATED MODEL) subplot(211)
hh=plot(t,u, t,y_sim, t,y);
grid on; axis tight;
legend('u - input voltage [v]','y_{sim} - simulated output - motor speed [RPM]','y - measured output -motor speed [RPM]');
xlabel('Time [s]')
set(gca,'FontSize',30);
set(hh(1),'LineWidth',2,'Color','red','LineStyle','-'); set(hh(2),'LineWidth',1,'Color','blue','LineStyle','-'); set(hh(3),'LineWidth',2,'Color','black','LineStyle','none','Marker','.');

%% EVALUATE MODEL FIT (Average error between measured and simulated output) AverageError = mean(y-y_sim);
subplot(212)
plot(t,y-y_sim);
grid on; axis tight;
title(['Average modelling error = ',num2str(AverageError,2),'[RPM]']); xlabel('Time [s]')
set(gca,'FontSize',30);

Least Squares for

4.4 Least Squares

▪ The graphical outputs are
shown
▪ From visually inspection, it is
clear the average modelling
error is very small

Least Squares for

4.5 Transfer Function; RPM V; Tau =; FiveTau =

The form here is given by:

Sample time: 0.01 seconds
Discrete-time transfer function.
Model Properties

%% Transfer function, time constant and system gain
a1 = theta(1);
b0 = theta(2)
Gd = tf([b0],[1 a1],0.01) %discrete-time transfer function

▪ The time constant, τ, and system
gain , K, for the 1st order transfer
function can be captured using
MATLAB, i.e.,

b = G.Denominator{1,1};
Tau = 1/b % 1 time constant (63.2% of yss)
FiveTau = 5*Tau % 5 time constants (99% of yss)
a = G.Numerator{1,1};
K = a(1,2)/b %system gain

Continuous-time transfer function.

▪ Using the MATLAB script, the
following is determined:

Least Squares for

# Least Squares for Parameter

# Contents

4.6 Summary; 4.1 Introduction……………………….2 4.2 Hardware………………………..5 4.3 Algorithm Design………….....6 4.4 Least Squares……………....9 4.5 Transfer Function……..12 4.6 Summary………….....13; 1. Introduction 2. Actuation; 3. Measurement 4. System Identification and Control

Control-Lab-in-a-Box (CLB) – 4.2

Estimation of a DC Motor

▪ The hardware required for capturing the input and output
data from an DC motor with an encoder has been presented
▪ Least squares algorithm has then been used to develop
discrete-time and continuous-time mathematical models of
the DC motor
▪ The error of the modelling has been determined, i.e.,
difference between the DC motor output data and the DC
motor mathematical model output

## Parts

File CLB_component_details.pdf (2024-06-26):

### Dr James E. Pickering

### Control-Lab-in-a-Box (CLB) Parts/Components Details

## 1.0 Storage Box

| Source
ID | Component | Unit Cost, Ex VAT [£] | Quantity | Total Cost, Ex VAT [£]

(UK)

1.1

Compartment storage box
(60 x 340 x 250mm) | 5.98 | 1 | 5.98 | CPC (https://cpc.farnell.com/duratool/d01931/assorter-340x250x60mm/dp/SG33199?st=electronic%20storage%20boxes)

1.2

Assorted storage cases, set
of 4 (310 x 377 x 265mm) | 24.95 | 1 | 24.95 | CPC (https://cpc.farnell.com/duratool/d01933/assorter-case-set-of-4/dp/SG33201?MER=sy-me-pd-mi-alte)

## 2.0 Electronic Components

ID | Component
Unit Cost, | Unit Cost, | Total Cost,
Inc VAT, | Ex VAT, | Ex VAT,
20% [£]
| | | 20% [£] | Quantity | 20% [£] | Source
2.1 | Arduino Mega 2560 | 43.13 | 35.94 | 1.00 | 35.94 | Rapid (https://www.rapidonline.com/arduino-mega2560-a000067-board-r3-73-4450)
2.2 | USB cable (Male USB A to
| Male USB B) | 3.14 | 2.62 | 1.00 | 2.62 | RS Components (https://uk.rs-online.com/web/p/usb-cables/1828831?gb=s)
2.3 | L298N dual H-bridge motor
| driver | 9.32 | 7.77 | 1.00 | 7.77 | Rapid (https://www.rapidonline.com/4tronix-l298n-dual-h-bridge-motor-driver-module-75-5013)

2.4

170 tie-points mini
breadboard (6 pack),
| required: 1 | 6.99 | 5.59 | 0.17 | 0.93 | Amazon UK (https://www.amazon.co.uk/ELEGOO-tie-points-Breadboard-Breadboards-Electronic/dp/B01N0YWIR7)
2.5 | Brushed geared DC motor
| with encoder | 10.82 | 8.66 | 1.00 | 8.66 | Amazon UK (https://www.amazon.co.uk/GBMQ-GM12BY20-Motor-Encoder-Magnetic-Electronic/dp/B0BG1R6FVP)
2.6 | Brushed geared DC motor | 13.61 | 11.34 | 1.00 | 11.34 | RS Components (https://uk.rs-online.com/web/p/dc-motors/8347644?gb=s)
2.7 | Brushless DC motor cooling
| fan | 7.38 | | 1.00 | 0.00 | Amazon UK (https://www.amazon.co.uk/s?k=Usongshine+Cooling+Fan+40+x+40)
2.8 | HC-SR04 ultrasonic sensor | 2.52 | 2.10 | 1.00 | 2.10 | RS Components (https://uk.rs-online.com/web/p/bbc-micro-bit-add-ons/2153181?gb=s)
2.9 | TMP36 temperature sensor | 2.99 | 2.16 | 1.00 | 2.16 | Mouser (https://www.mouser.co.uk/ProductDetail/Analog-Devices/TMP36GT9Z?qs=WIvQP4zGanhT97N47MSoHw%3D%3D&mgh=1&vip=1)
2.10 | 220 Ohm resistor (pack of
| 10), required: 3 | 1.27 | 1.06 | 0.30 | 0.32 | RS Components (https://uk.rs-online.com/web/p/through-hole-resistors/7077666?gb=s)
2.11 | 2.9 V LED 5mm (pack of 5),
| required: 3 | 1.81 | 1.51 | 0.60 | 0.91 | RS Components (https://uk.rs-online.com/web/p/leds/2285988?gb=s)
2.12 | 9V power jack | 0.64 | 0.53 | 1.00 | 0.53 | RS Components (https://uk.rs-online.com/web/p/battery-contacts/1854788?gb=s)
2.13 | 9V rechargeable battery with
| micro-c cable (pack of 2),
| required: 1 | 13.99 | 11.19 | 0.50 | 5.60 | Amazon UK (https://www.amazon.co.uk/PAISUE-Rechargeable-Lithium-ion-Multimeter-Microphone/dp/B09WKFZPN7?sp_csd=d2lkZ2V0TmFtZT1zcF9tdGY)
2.14 | Male-to-male breadboard
| wires (pack of 10), required:
| 8 | 0.96 | 0.80 | 0.80 | 0.64 | RS Components (https://uk.rs-online.com/web/p/breadboard-jumper-wires/2832658?gb=s)
2.15 | Male-to-female breadboard
| wires , required: 6 | 0.96 | 0.80 | 0.60 | 0.48 | RS Components (https://uk.rs-online.com/web/p/breadboard-jumper-wires/2832656?gb=s)
Total | | | | | 79.99

## 3.0 Rapid Prototyping

ID Component

Unit Cost,

| Ex VAT [£] | Quantity | Total Cost,
| | | Ex VAT [£] | Manufacturing
| | | | method

3.1

Base 1 (acrylic),
98 x 54 x 3mm | 0.15 | 1 | 0.15 | Laser cutter

3.2

Base 2 (acrylic),
209 x 70 x 3mm | 0.45 | 1 | 0.45 | Laser cutter

3.3

DC motor mount
(PLA) | 0.05 | 1 | 0.05 | 3D printer
3.4 Wheel (PLA) | 0.17 | 1 | 0.17 | 3D printer

3.5

Ultrasonic sensor
and LEDs mount
(PLA) | 0.15 | 1 | 0.15 | 3D printer
3.6 Legs (PLA) | 0.07 | 2 | 0.14 | 3D printer
| Total | | 1.11

## 4.0 Nuts and Bolts

ID | Component | Required
Unit Cost, | Total Cost,
Ex VAT, 20% | Ex VAT, 20%
| | [£] | Quantity | [£] | Source (UK)

4.10

Hex threaded Spacer,
M3 12mm (pack of 25) 12.00 | 11.55 | 0.48 | 5.54 | Rapid (https://www.rapidonline.com/r-tech-524389-hex-threaded-f-f-a2-st-st-spacers-m3-12mm-pk-25-52-4389)

4.20

Hex Threaded Spacer,
M3 x 30mm | 4.00 | 0.26 | 4.00 | 1.04 | CPC (https://cpc.farnell.com/ettinger/00503303/brass-threaded-hex-spacer-female-m3-x-30mm/dp/pc02628?msclkid=f416670a501a1a3346fb01709422fabe)

4.30

Nylon locking nut, M3
(order of 6) | 4.00 | 0.24 | 4.00 | 0.96 | Accu (https://www.accu.co.uk/hexagon-nylon-locking-nuts/7957-HNN-M3-A4?uk_google_shopping=1&c=3&msclkid=c5a38e91120f18506e78e8ebaa6d1ec6)

4.40

Bolt, 6mm, M3 (pack
of 100) | 18.00 | 4.45 | 0.18 | 0.80 | Rapid (https://www.rapidonline.com/r-tech-337089-pozi-pan-head-a2-stainless-steel-screws-m3-6mm-pack-of-100-33-7089)

4.50

Bolt, 10mm, M3 (pack
of 100) | 8.00 | 2.68 | 0.08 | 0.21 | Rapid (https://www.rapidonline.com/toolcraft-phillips-raised-head-screws-din-7985-steel-4-8-m3-x-10mm-pack-of-100-51-3331)

4.60

Bolt,16mm, M3 (pack
of 100) | 8.00 | 2.07 | 0.08 | 0.17 | CPC (https://cpc.farnell.com/tr-fastenings/m3-16-prstmc-z100/m3-x-16mm-steel-bzp-pan-head-pozidriv-machine-screws-100-pack/dp/fn05256?gad_source=1)
4.70 Nuts, M3 (pack of 100) 4.00 | 1.26 | 0.04 | 0.05 | Rapid (https://www.rapidonline.com/affix-steel-nuts-bzp-m3-pack-of-100-33-1710)
4.80 Bolt, 10mm, M1.4 | 4.00 | 0.62 | 4.00 | 2.48 | Accu (https://www.accu.co.uk/phillips-pan-head-screws/65351-SIP-M1-4-10-A2?uk_google_shopping=1&c=3&gad_source=1)

4.90

Nuts, M1.4 (pack of
250) | 4.00 | 143.19 | 0.02 | 2.29 | RS Components (https://uk.rs-online.com/web/p/hex-nuts/1795725)
Total | | | | 13.55

## 5.0 Primary Tools

ID | Component | Unit Cost
| | [£] | Quantity | Total
| | | | Cost, Ex
| | | | VAT [£] | Source (UK)
5.1 | Philips screwdriver (75mm x No 0) | 2.50 | 1 | 2.50 | Rapid (https://www.rapidonline.com/rapid-75-x-no-0-phillips-screwdriver-86-0450)
5.2 | Flat bladed screwdrvier (75 x 3mm) 2.23 | 1 | 2.23 | Rapid (https://www.rapidonline.com/rapid-75-x-3mm-flat-bladed-screwdriver-86-0400)
5.3 | Hexagon nut driver, 5.5mm tip | 7.74 | 1 | 7.74 | RS Components (https://uk.rs-online.com/web/p/nut-drivers/8759337?gb=s)
Total | | | | 12.47

## 6.0 Additional Tools

ID | Component | Unit Cost
| | [£] | Quantity | Total
| | | | Cost, Ex
| | | | VAT [£] | Source (UK)
6.1 | Wire cutters | 8.19 | 1 | 8.19 | RS Components (https://uk.rs-online.com/web/p/wire-strippers/2834633?gb=s)
6.2 | Soldering iron | 30.40 | 1 | 30.40 | Rapid (https://www.rapidonline.com/antex-s58j4h8-xs25w-soldering-iron-230v-with-silicone-cable-and-13a-plug-85-1145)
6.3 | Solder | 2.77 | 1 | 2.77 | RS Components (https://uk.rs-online.com/web/p/solder/0273255?gb=s)
6.4 | Heat shrink tubing (1.6mm) | 1.24 | 1 | 1.24 | RS Components (https://uk.rs-online.com/web/p/heat-shrink-tubing/7004620?gb=s)
6.5 | Heat shrink tubing (3.2mm) | 10.55 | 1 | 10.55 | Rapid (https://www.rapidonline.com/Cables-Connectors/3-2mm-Black-11m-Mini-Reel-Heat-Shrink-03-0270)
Total | | | | 53.15

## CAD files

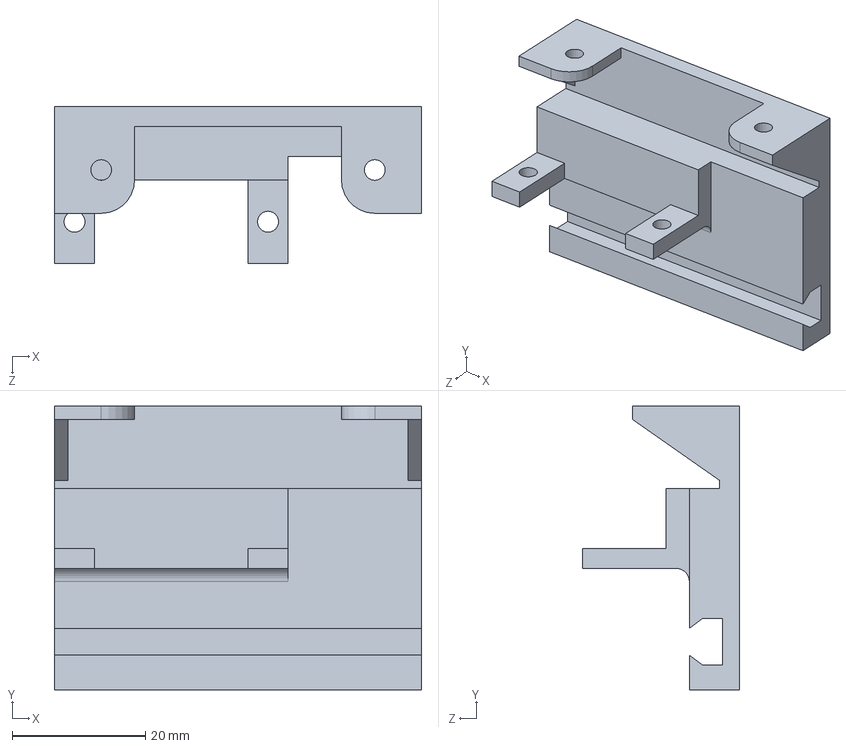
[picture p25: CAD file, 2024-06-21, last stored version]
FVT-servo plate.SLDPRT
55.0 x 42.5 x 23.5 mm

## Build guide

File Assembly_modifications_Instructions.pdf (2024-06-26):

### Dr James E. Pickering

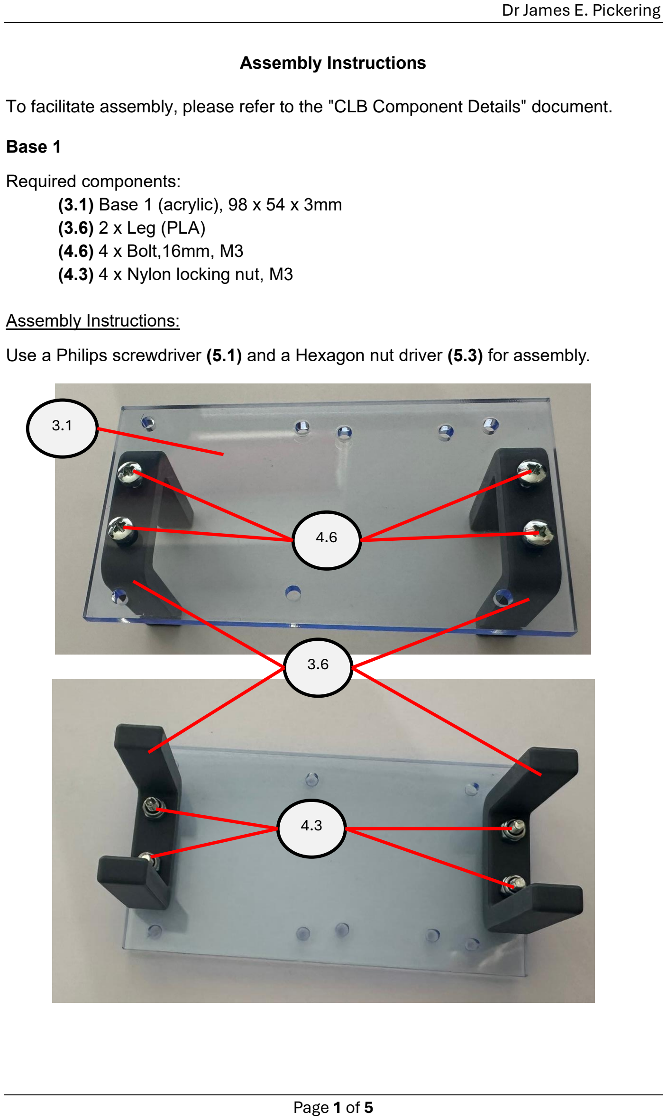
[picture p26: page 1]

Assembly Instructions

To facilitate assembly, please refer to the "CLB Component Details" document.

Base 1

Required components:
(3.1) Base 1 (acrylic), 98 x 54 x 3mm
(3.6) 2 x Leg (PLA)
(4.6) 4 x Bolt,16mm, M3
(4.3) 4 x Nylon locking nut, M3

Assembly Instructions:

Use a Philips screwdriver (5.1) and a Hexagon nut driver (5.3) for assembly.

3.1

3.6

4.6

4.3

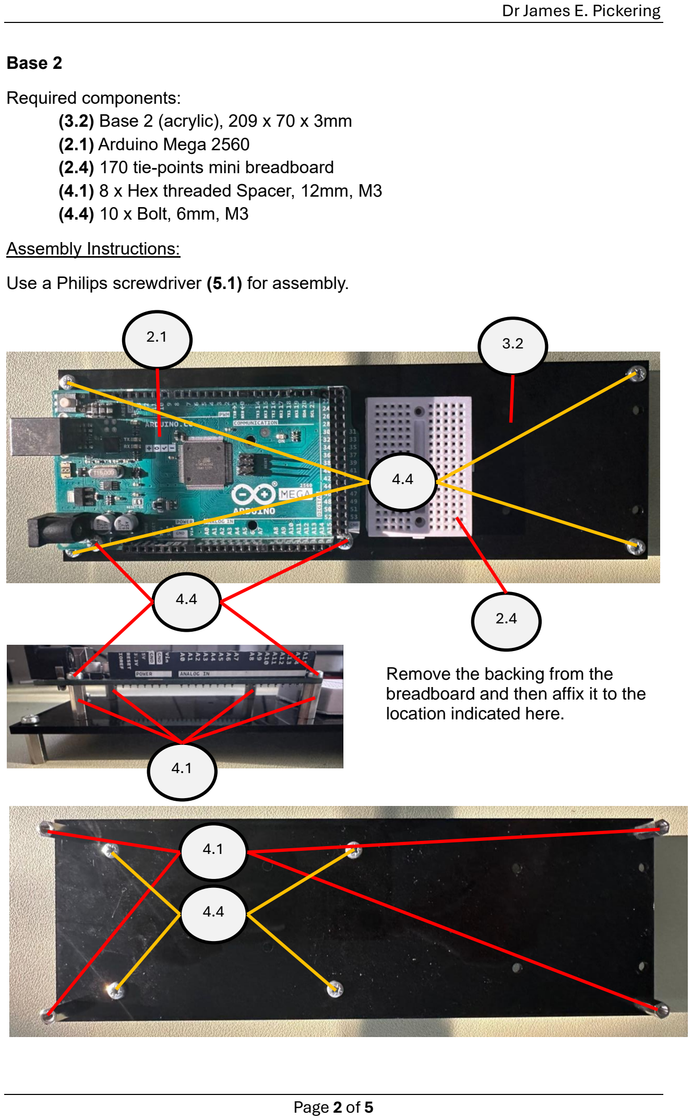
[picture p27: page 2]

Base 2

Required components:
(3.2) Base 2 (acrylic), 209 x 70 x 3mm
(2.1) Arduino Mega 2560
(2.4) 170 tie-points mini breadboard
(4.1) 8 x Hex threaded Spacer, 12mm, M3
(4.4) 10 x Bolt, 6mm, M3

Assembly Instructions:

Use a Philips screwdriver (5.1) for assembly.

Remove the backing from the breadboard and then affix it to the location indicated here.

3.2 2.1

2.4

4.1

4.4

4.4

4.1

4.4

Ultrasonic sensor and LEDs mount (PLA)

Required components:
(2.8) HC-SR04 ultrasonic sensor
(3.5) Ultrasonic sensor and LEDs mount (PLA)
(4.8) 4 x Nuts, M1.4
(4.9) 4 x Bolt, 10mm, M1.4

Assembly Instructions:

Use a Philips screwdriver (5.1) for assembly.

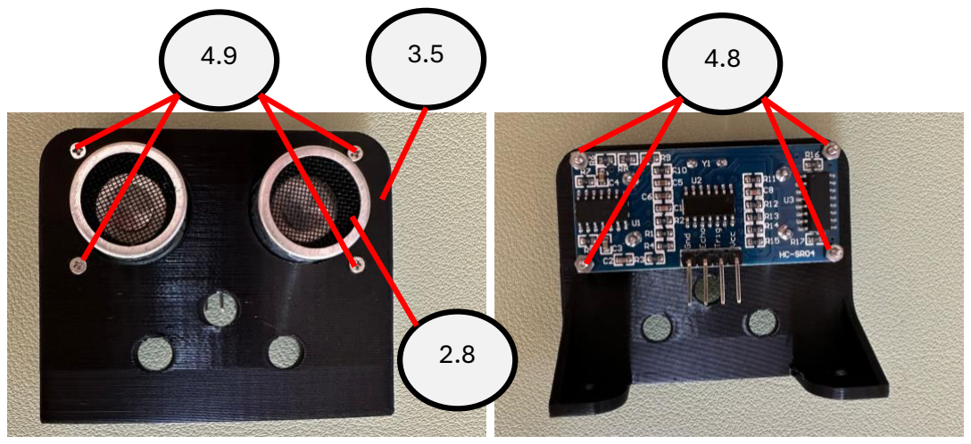
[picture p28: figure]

### ‘Difficult’ connection

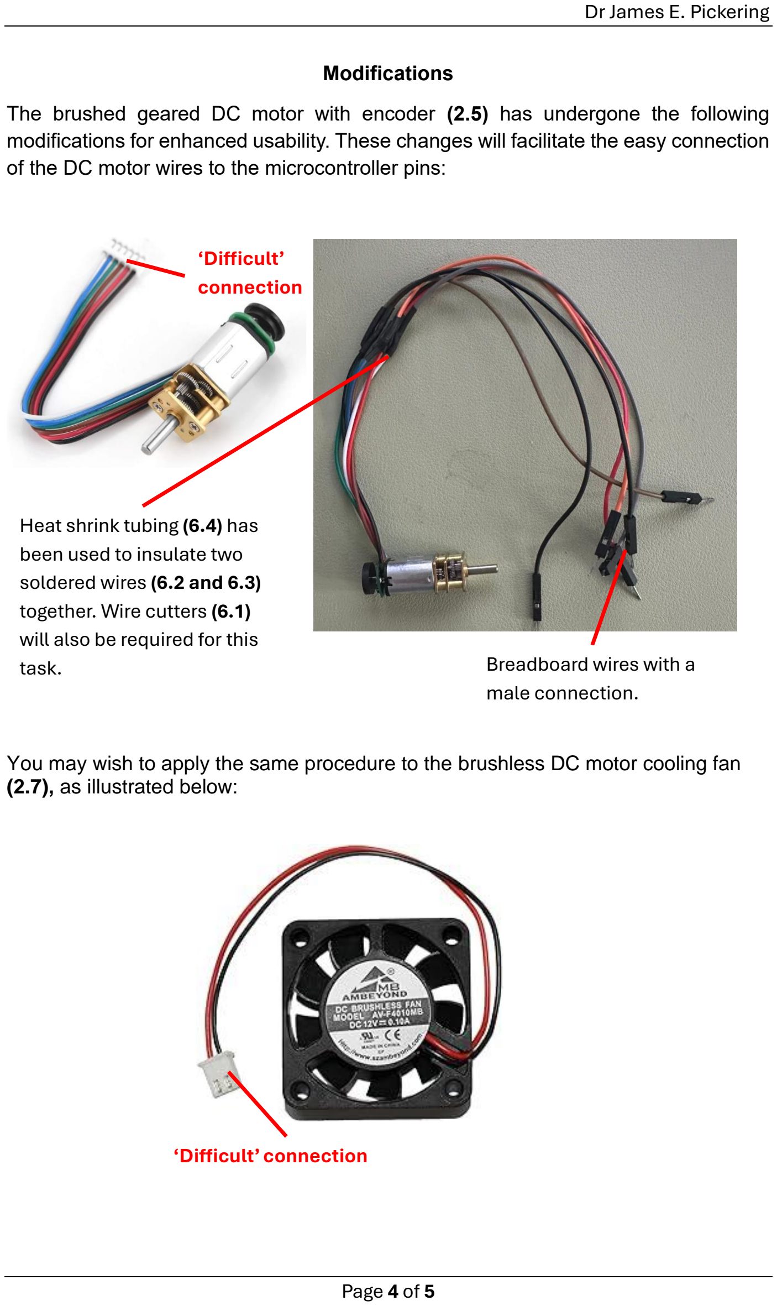
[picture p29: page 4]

Modifications

The brushed geared DC motor with encoder (2.5) has undergone the following modifications for enhanced usability. These changes will facilitate the easy connection of the DC motor wires to the microcontroller pins:

You may wish to apply the same procedure to the brushless DC motor cooling fan (2.7), as illustrated below:

### Heat shrink tubing (6.4) has been used to insulate two soldered wires (6.2 and 6.3) together. Wire cutters (6.1) will also be required for this

task. | Breadboard wires with a
| male connection.

### ‘Difficult’ connection

For the brushed geared DC motor with encoder (2.5), it is advisable to reinforce the area where the wires connect to the board. This can be achieved by using superglue or electrical installation tape to secure all six wires together, thereby strengthening the connections.

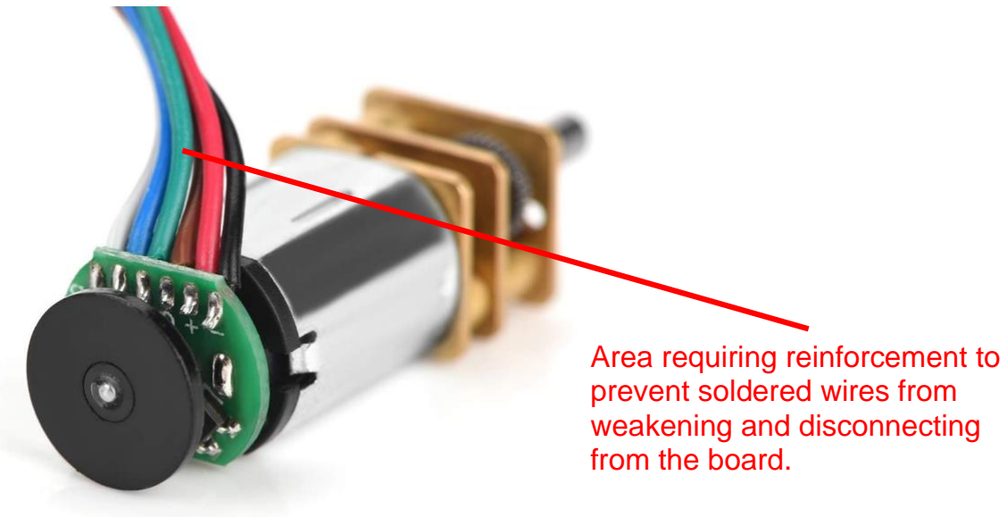
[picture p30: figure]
Area requiring reinforcement to prevent soldered wires from weakening and disconnecting from the board.

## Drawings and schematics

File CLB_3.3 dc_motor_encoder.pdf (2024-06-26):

# DC Motor with an Encoder

# Contents

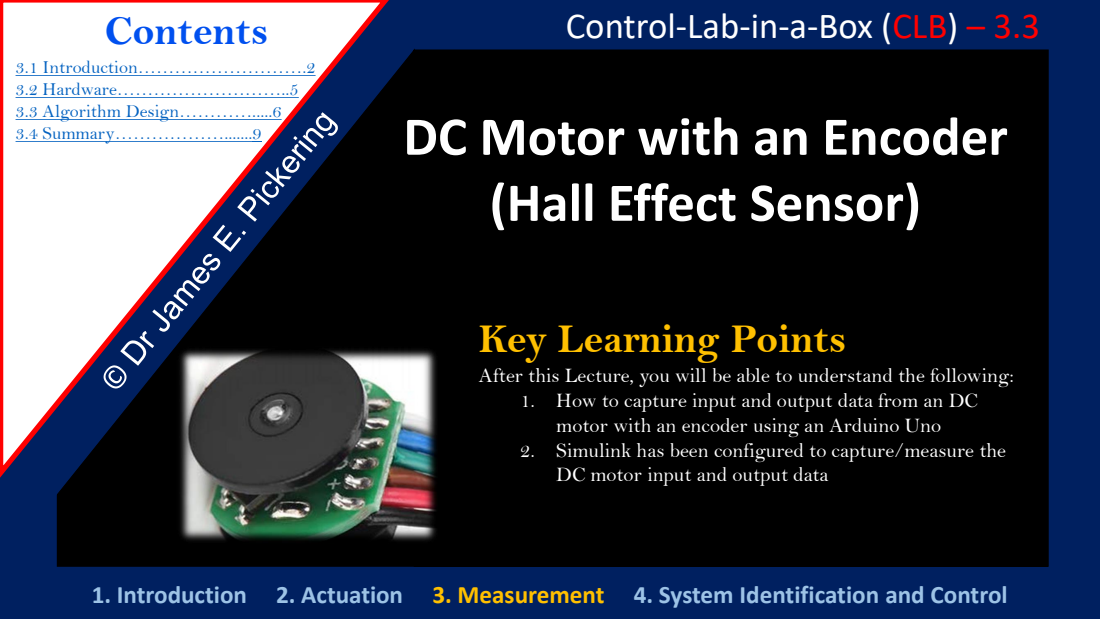
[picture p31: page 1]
1. Introduction 2. Actuation; 3. Measurement 4. System Identification and Control

Control-Lab-in-a-Box (CLB) – 3.3

(Hall Effect Sensor)

Key Learning Points

After this Lecture, you will be able to understand the following:
1. How to capture input and output data from an DC
motor with an encoder using an Arduino Uno
2. Simulink has been configured to capture/measure the
DC motor input and output data

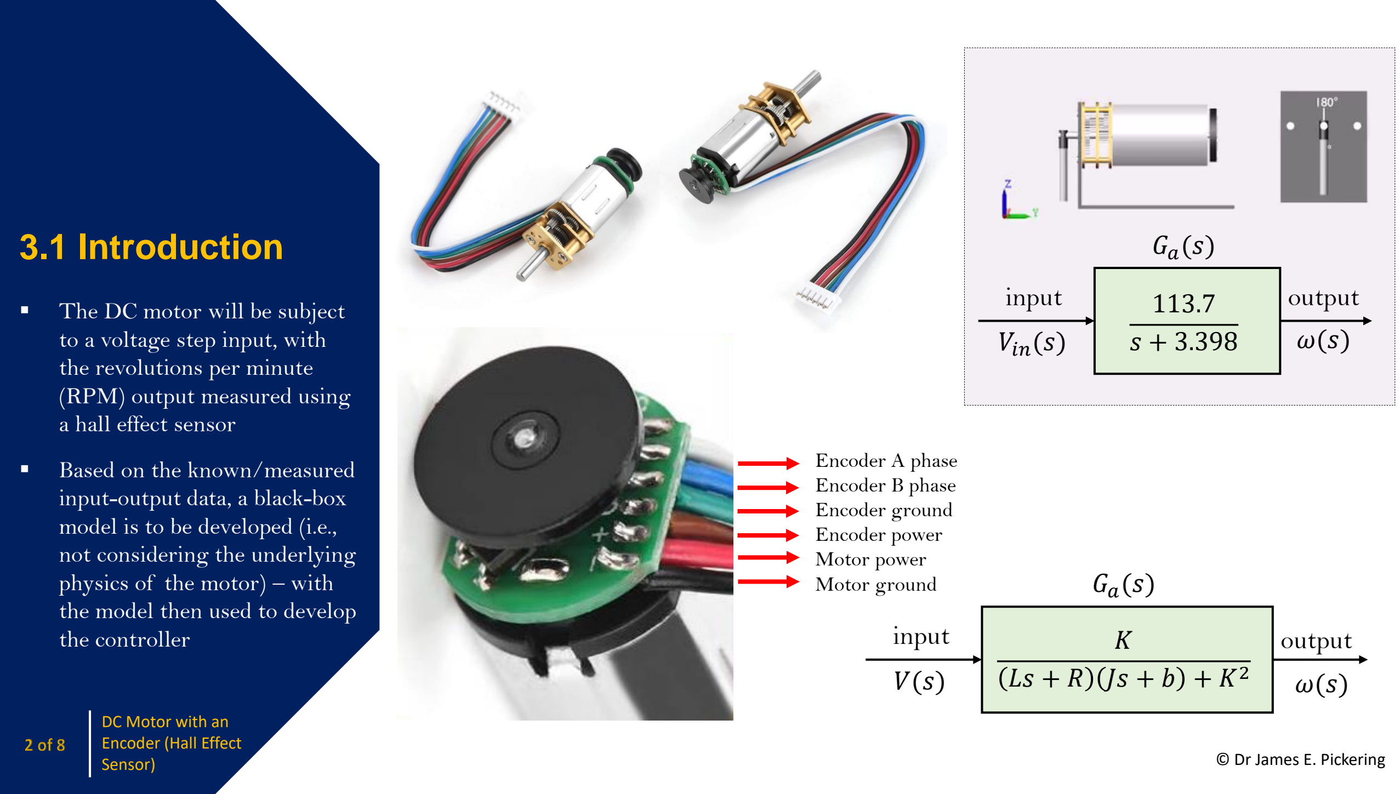
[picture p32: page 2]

### 3.1 Introduction ▪ The DC motor will be subject

to a voltage step input, with the revolutions per minute (RPM) output measured using a hall effect sensor

- Based on the known/measured input

-output data, a black

-box
model is to be developed (i.e., not considering the underlying physics of the motor)

– with
the model then used to develop the controller

DC Motor with an
Encoder (Hall Effect
Sensor) | © Dr James E. Pickering

Encoder A phase
Encoder B phase
Encoder ground
Encoder power
Motor power
Motor ground

K
Ls

+

R Js

+

b

+

K

2

input

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
# output ω(s)

113.7
s

+

3.398

input Vin(s)

output

G
a

(

s

)

## 3.1 Introduction

- A Hall effect sensor detects a magnetic field
- The output voltage of a Hall sensor is directly proportional to the strength of the field. It is named for the American
physicist Edwin Hall.
- By detecting the passing of a magnet, the Hall effect sensor generates a pulse-train output

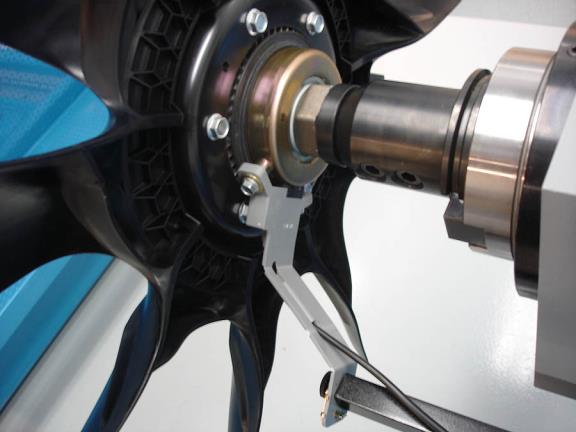
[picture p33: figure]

© Dr James E. Pickering

- Hall effects sensors are commonly used to time the speed of wheels and shafts, such as for internal combustion engine ignition timing, tachometers and anti-lock braking systems
- Hall effect sensors are used in brushless DC electric motors to detect the position
- Employing an offset Hall effect sensor can generate a quadrature output for determining the direction of the motion

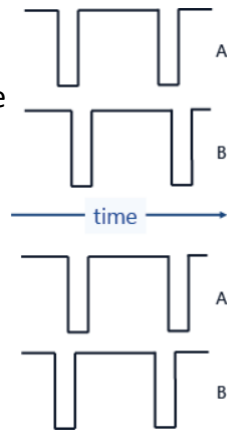
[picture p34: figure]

Clockwise

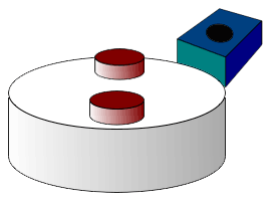
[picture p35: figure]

Anti-clockwise

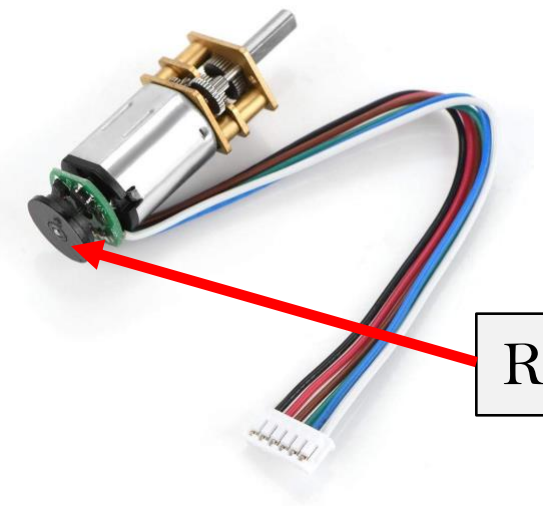
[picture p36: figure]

DC Motor with an | Resolution of 12 impulses per revolution

Sensor)

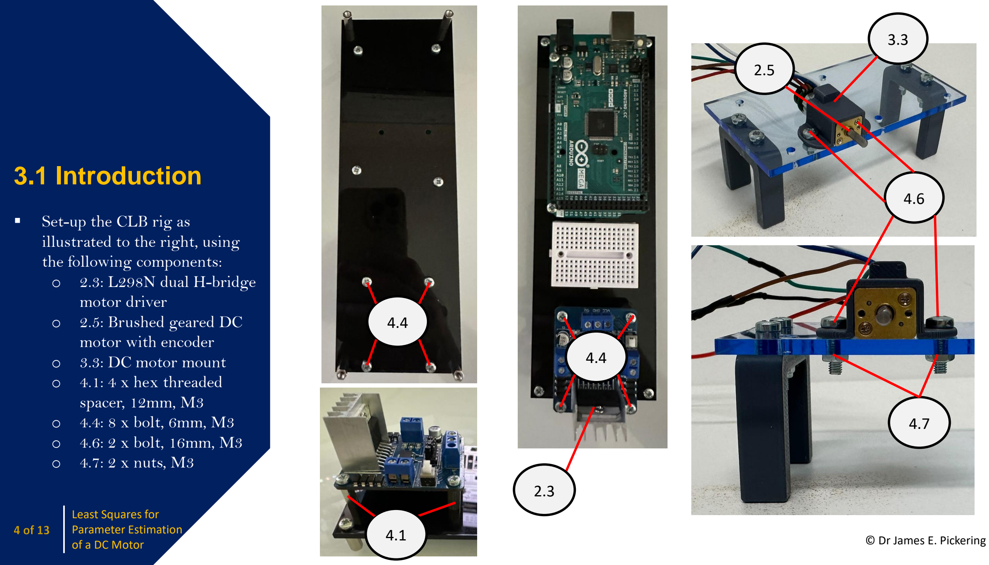
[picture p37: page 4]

### 3.1 Introduction ▪ Set-up the CLB rig as

illustrated to the right, using
the following components: o | | | 2.3: L298N dual H-bridge
| | | motor driver
- 2.5: Brushed geared DC
| | | motor with encoder
- | 3.3: DC motor mount o | 4.1: 4 x hex threaded
| | | spacer, 12mm, M3
- | 4.4: 8 x bolt, 6mm, M3 o | 4.6: 2 x bolt, 16mm, M3 o | 4.7: 2 x nuts, M3

Least Squares for
Parameter Estimation
of a DC Motor

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
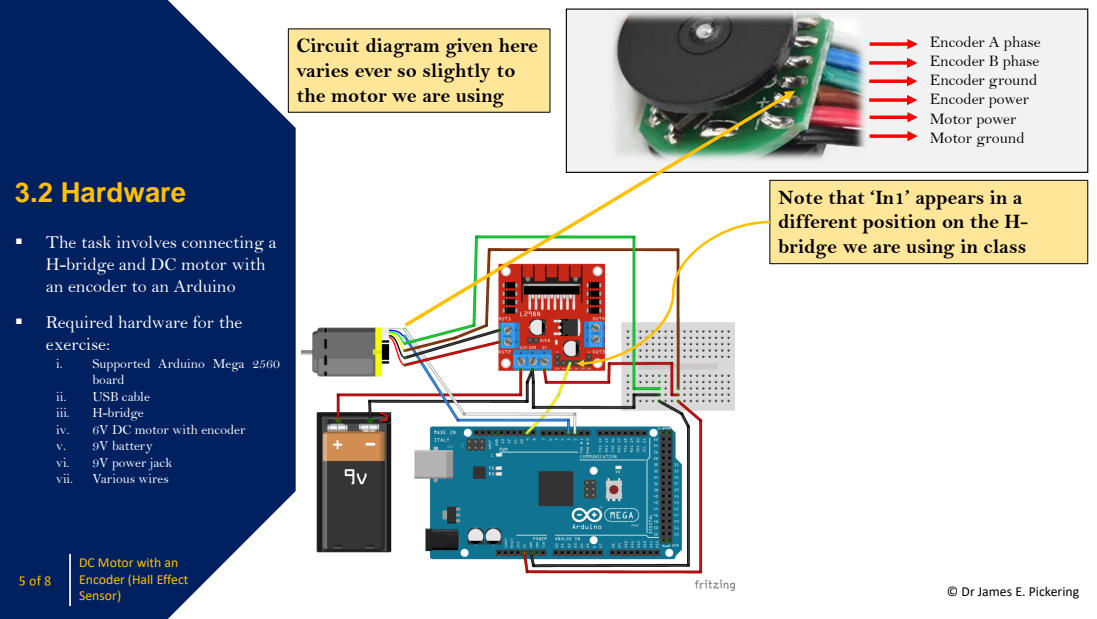
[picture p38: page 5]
3.2 Hardware; USB cable; iii.; H-bridge; 6V DC motor with encoder; 9V power jack; vii.; Various wires; Encoder A phase Encoder B phase Encoder ground Encoder power Motor power Motor ground; Sensor)

Circuit diagram given here
varies ever so slightly to
the motor we are using

Note that ‘In1’ appears in a
different position on the H-
bridge we are using in class

▪ The task involves connecting a
H-bridge and DC motor with
an encoder to an Arduino

▪ Required hardware for the
exercise:
i. Supported Arduino Mega 2560
board
v. 9V battery

DC Motor with an

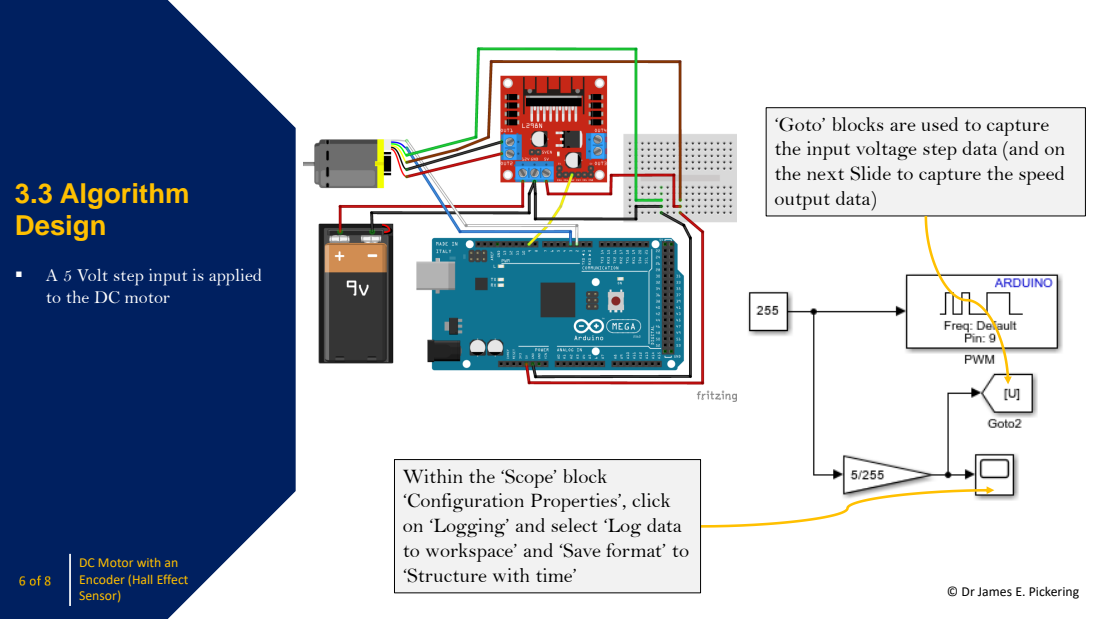
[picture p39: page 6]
3.3 Algorithm Design; Sensor)

‘Goto’ blocks are used to capture
the input voltage step data (and on
the next Slide to capture the speed
output data)

▪ A 5 Volt step input is applied
to the DC motor

Within the ‘Scope’ block
‘Configuration Properties’, click
on ‘Logging’ and select ‘Log data
to workspace’ and ‘Save format’ to
‘Structure with time’

DC Motor with an

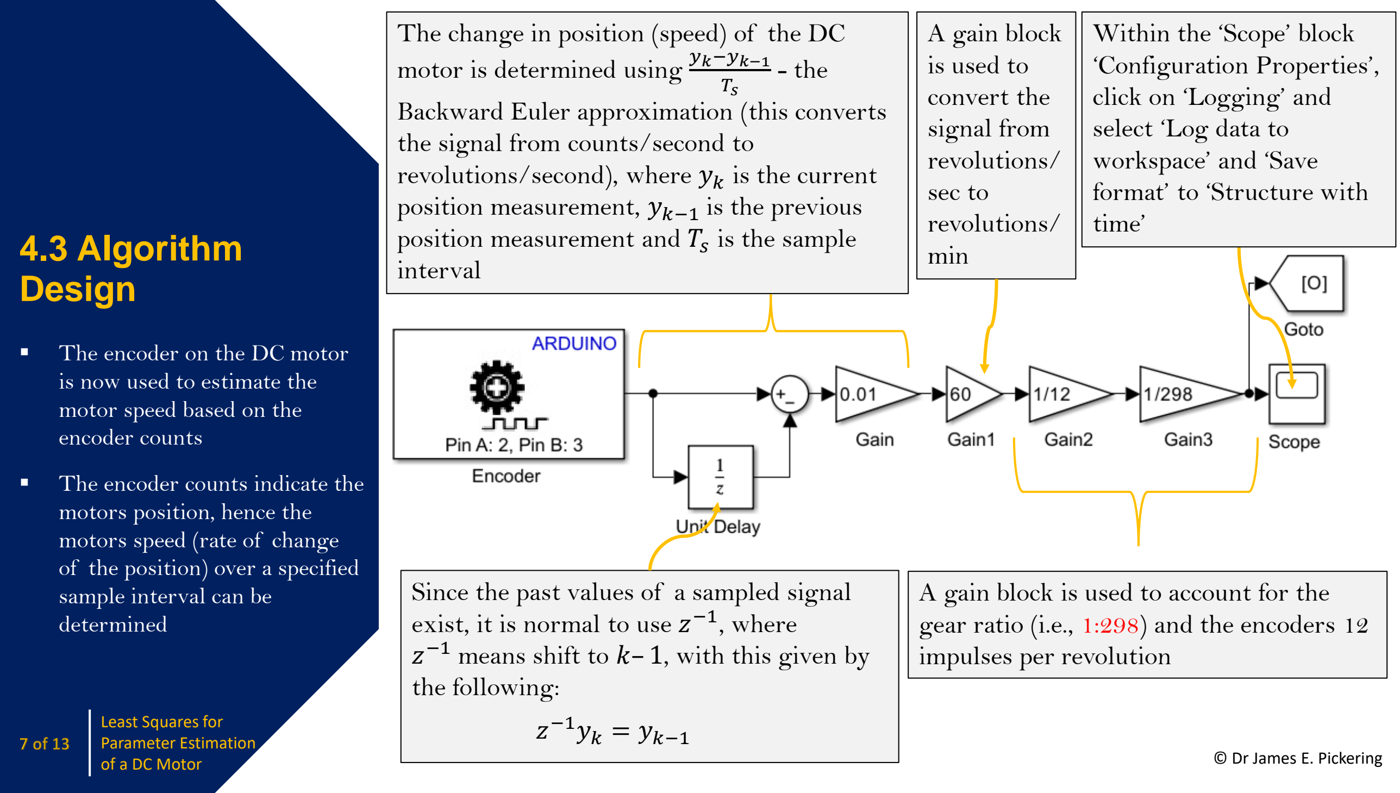
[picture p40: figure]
4.3 Algorithm Design; ▪ The encoder on the DC motor is now used to estimate the motor speed based on the encoder counts; ▪ The encoder counts indicate the motors position, hence the motors speed (rate of change of the position) over a specified sample interval can be determined; motor is determined using yk−yk−1; - the; Backward Euler approximation (this converts the signal from counts/second to; position measurement and Ts; is the sample; interval; Least Squares for Parameter Estimation of a DC Motor; exist, it is normal to use z; , where; z the following: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

The change in position (speed) of the DC

revolutions/second), where yk is the current position measurement, yk−1 is the previous

Since the past values of a sampled signal

−1 means shift to k– 1, with this given by gear ratio (i.e., 1:298) and the encoders 12
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

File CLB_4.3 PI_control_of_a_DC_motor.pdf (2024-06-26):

# DC Motor Proportional and

# Contents

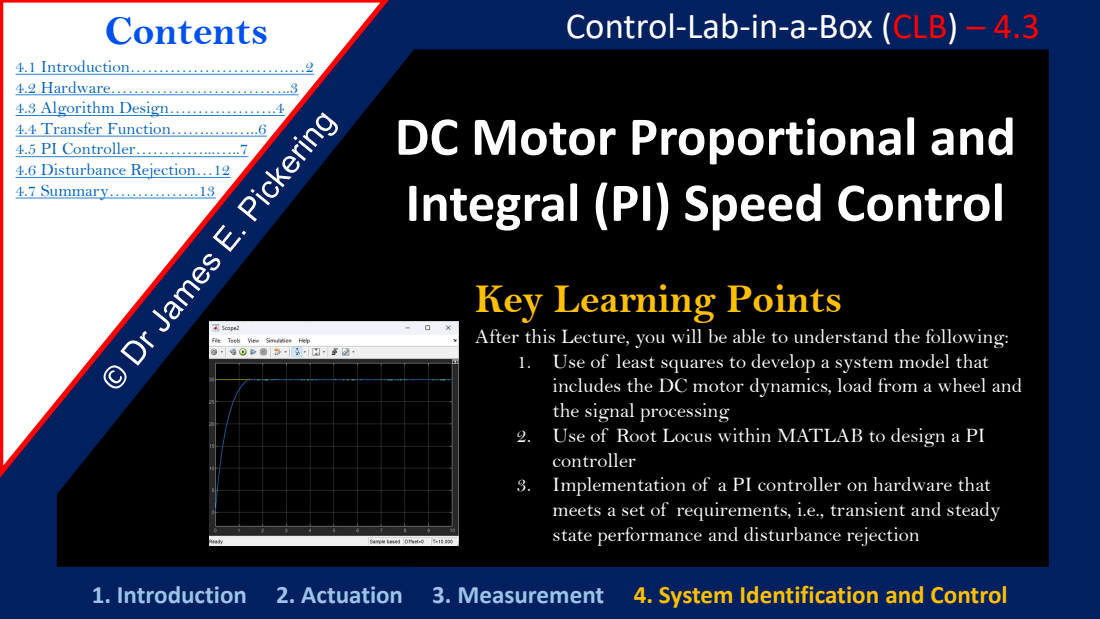
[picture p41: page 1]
4.6 Disturbance Rejection…12; 1. Introduction 2. Actuation; 3. Measurement 4. System Identification and Control

Control-Lab-in-a-Box (CLB) – 4.3

Integral (PI) Speed Control

Key Learning Points

After this Lecture, you will be able to understand the following:
1. Use of least squares to develop a system model that
includes the DC motor dynamics, load from a wheel and
the signal processing
2. Use of Root Locus within MATLAB to design a PI
controller
3. Implementation of a PI controller on hardware that
meets a set of requirements, i.e., transient and steady
state performance and disturbance rejection

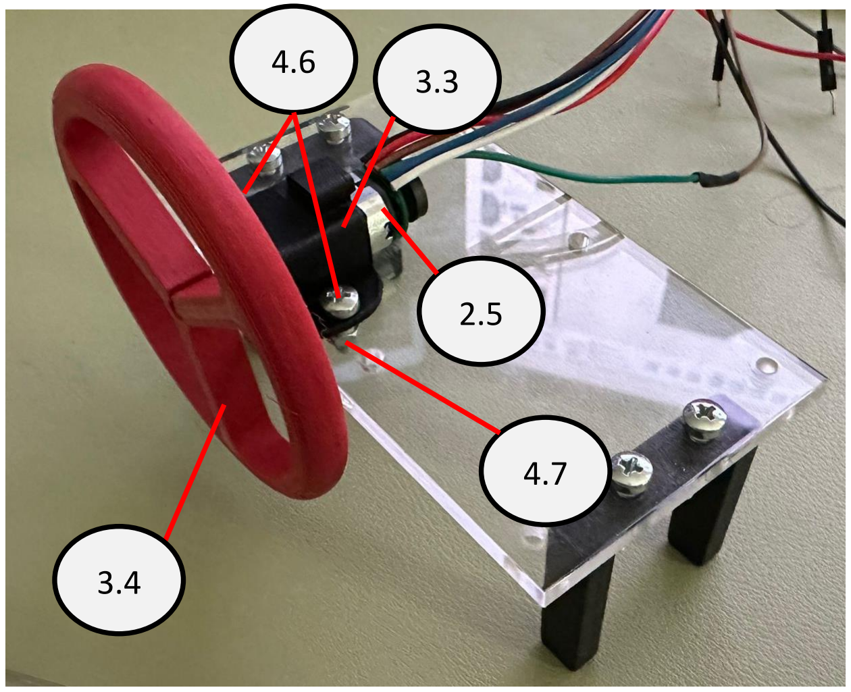
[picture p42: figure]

## 4.1 Introduction

- To start, a system model is going to be developed that includes the DC motor
dynamics, a wheel and a low pass filter, denoted G′(s)
- Set-up the CLB rig as illustrated to the right, using the following components:
- 2.5: Brushed geared DC
motor with encoder
- 3.3: DC motor mount
- 3.4 Wheel
- 4.6: 2 x bolt, 16mm, M3
- 4.7: 2 x nuts, M3

reference; PID(z); output

© Dr James E. Pickering

- The developed transfer
function, denoted G′(s) will therefore capture the DC
motor dynamics including the wheel and low pass filter
- The transfer function G′(s) will then be used to design the PID controller

DC Motor Proportional
and Integral (PI)
Speed Control

Circuit diagram given here varies ever so slightly to the motor we are using; 4.2 Hardware; ▪ Same hardware used is in the system identification exercise; ▪ The task involves connecting a H-bridge and DC motor with an encoder to an Arduino; ▪ Required hardware for the exercise:; i. Supported Arduino Mega 2560 board; USB cable; iii.; H-bridge; 6V DC motor with encoder; v. 9V battery; 9V power jack; vii.; Various wires; Encoder B phase Encoder A phase Encoder ground Encoder power Motor power Motor ground; Note that ‘In1’ appears in a different position on the H-bridge we are using in class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
4.3 Algorithm; Design ▪; To recall how to capture the

data (etc.), see the ‘Least
Squares for Parameter
Estimation of a DC Motor’
notes

▪ Low pass filter is designed
using a time constant,

Low pass filter
introduced

DC Motor Proportional

4.3 Algorithm; Design ▪; Use the MATLAB script from

the ‘Least Squares for Parameter
Estimation of a DC Motor’
notes

▪ The graphical outputs are
shown
▪ From visually inspection, it is
clear the average modelling
error is very small

DC Motor Proportional

4.4 Transfer Function; RPM; theta = -0.9809 0.1676 >> untitled6 b0 = 0.1676 Gd = 0.1676 ---------- z - 0.9809 Sample time: 0.01 seconds Discrete-time transfer function. Model Properties G = 16.92 -------- s + 1.93 Continuous-time transfer function. Model Properties Tau = 0.5182 FiveTau = 2.5911 K = 8.7669

The form here is given by:

%% Transfer function, time constant and system gain
a1 = theta(1);
b0 = theta(2)
Gd = tf([b0],[1 a1],0.01) %discrete-time transfer function

▪ The time constant, τ, and system
gain , K, for the 1st order transfer
function can be captured using
MATLAB, i.e.,

b = G.Denominator{1,1};
Tau = 1/b % 1 time constant (63.2% of yss)
FiveTau = 5*Tau % 5 time constants (99% of yss)
a = G.Numerator{1,1};
K = a(1,2)/b %system gain

▪ Using the MATLAB script, the
following is determined:

Interesting: significant change to the time
constant of the transfer function, i.e.,

DC Motor Proportional
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

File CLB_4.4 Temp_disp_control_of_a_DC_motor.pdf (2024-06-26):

Contents | Embedded Control (CLB) – 4.4

# DC Motor Proportional and

Control; 1. Introduction 2. Actuation; 3. Measurement 4. System Identification and Control

4.2 DC Motor Wheel Control (On/Off) due to

4.3 DC Motor Fan Control (On/Off) due to

4.4 DC Motor Fan Control (On/Off) due

Integral (PI) and On/Off Speed

4.5 DC Motor Fan Control (On/Off)
due to Obstacle and Temperature..9

Key Learning Points

After this Lecture, you will be able to understand the following:
1. Use of the MATLAB function block for applying logic
to control systems
2. The use of the MATLAB function block to control the
on/off motion of a DC motor due to temperature and
obstacles


## 4.1 Introduction

- On/off control for a DC motor will be designed based on the following:
i. Temperature control
ii. Obstacle avoidance
- At this point, you should be well-versed in setting up the control-lab-in-a-box (CLB) for each exercise. Consequently, detailed instructions are not provided here. However, if you need a refresher, please refer to the previous notes.

© Dr James E. Pickering

DC Motor Proportional
and Integral (PI) and
On/Off Speed Control

Control-Lab-in-a-Box (CLB): DC Motor PI Speed Control and Temperature Control

Control-Lab-in-a-Box (CLB): DC Motor PI Speed Control with Obstacle Avoidance

DC motor off when; function u2 = fcn(T, u1); if T >= 40; u2 = 0; else T < 40; u2 = u1;; end

Test the below before implementing this (detailed
on the next slide).

4.2 DC Motor Wheel
Control (On/Off)
due to Temperature

▪ The MATLAB Function block
is used to define the following:
i. DC motor on when
temperature
measurement is below
40 degrees Celsius
measurement is equal or
above 40 degrees
Celsius

DC Motor Proportional


## 4.2 DC Motor Wheel Control (On/Off) due to Temperature

- Simulink diagram is given for the operation of the DC motor wheel control (on/off) due to the ranges in temperature
detailed on the previous slide

DC Motor Proportional

### Developed in CLB 3.1

### Developed in CLB 3.3 and CLB 4.3

### ‘Curved’ side of the temperature sensor ‘sits’ within the DC motor bracket

DC motor fan is off when; function u3 = fcn(T); else T < 25; u3 = 0;; end

Test the below before implementing this (detailed
on the next slide).

4.3 DC Motor Fan
Control (On/Off) due
to Temperature

▪ The MATLAB Function block is
used to define the following:
i. DC motor fan is on when
temperature measurement
is above or equal to 25
degrees Celsius
is below 25 degrees Celsius

DC Motor Proportional

## 4.3 DC Motor Fan Control (On/Off) due to Temperature

- Simulink diagram is given for the operation of the DC motor wheel control (on/off) and the DC motor with fan due to the ranges in temperature detailed on the previous slide

DC Motor Proportional


### After running the above script, the temperature

control will now operate.

DC motor off when; function u5 = fcn(d, u4); if d >= 0.1; u5 = u4; else d < 0.1; u5 = 0;; end

Test the below before implementing this (detailed
on the next slide).

4.4 DC Motor Fan
Control (On/Off) due
to Obstacle

▪ The MATLAB Function block
is used to define the following:
i. DC motor on when
distance measurement is
above or equal to 0.1
meters
below 0.1 meters

DC Motor Proportional


## 4.4 DC Motor Fan Control (On/Off) due to Obstacle

- Simulink diagram is given for the operation of the DC motor wheel control (on/off) and the due to the ranges in distance measurements detailed on the previous slide

DC Motor Proportional

### Developed in CLB 3.3 and CLB 4.3

### Developed in CLB 3.2

### After running the above script, the obstacle

avoidance will now operat.


## 4.5 DC Motor Fan Control (On/Off) due to Obstacle and Temperature

- All three of the MATLAB
Function blocks are combined here

DC Motor Proportional

### Test the below before implementing this (detailed

on the next slide).

## 4.5 DC Motor Fan Control (On/Off) due to Obstacle and Temperature

- Simulink diagram is given for the operation of the DC motor wheel control (on/off) and DC motor fan (on/off) due to the ranges in distance
measurements and temperature measurements detailed on the previous slide

DC Motor Proportional

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

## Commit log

2024-06-21 Create laser_cutting_STL_files
2024-06-21 Rename Laser_cutting_parts to 2. Laser_cutting_parts
2024-06-21 3D printing CAD files
    Following three files are attached:
2024-06-25 CAD files for 3D printing
2024-06-25 CAD files for 3D printing
    Solidworks 2023 and STL 'raw' files are attached for the following components to be 3D printed:
    * DC motor mount
    * Wheel
    * Ultrasonic sensor and LEDs mount
    * Leg
2024-06-25 CAD files to be laser cut
    Solidworks 2023 and STL 'raw' files are attached for the following components to be laser cut:
    * Board 1
    * Board 2
2024-06-25 Parts/components that need to be sourced
    Details of the following are provided:
    * 1.0 Storage Box
    * 2.0 Electronic Components
    * 3.0 Rapid Prototyping
    * 4.0 Nuts and Bolts
    * 5.0 Primary Tools
    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
